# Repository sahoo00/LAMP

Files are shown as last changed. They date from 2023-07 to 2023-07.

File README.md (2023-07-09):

# LAMP
A RT-LAMP device for quantitative mRNA measurement at home

## General Info
This folder has EAGLE files for a hardware device that can measure mRNA
at home. There are two modules: Camera and LAMP. Arduino codes, 
Board and Schematic files
for both these modules are provided. CAM processor outputs of all the files
are provided in CAMOutputs.

## Software requirements
Project is created with
* EAGLE
* Adobe Illustrator
* Fusion 360
* Arduino IDE

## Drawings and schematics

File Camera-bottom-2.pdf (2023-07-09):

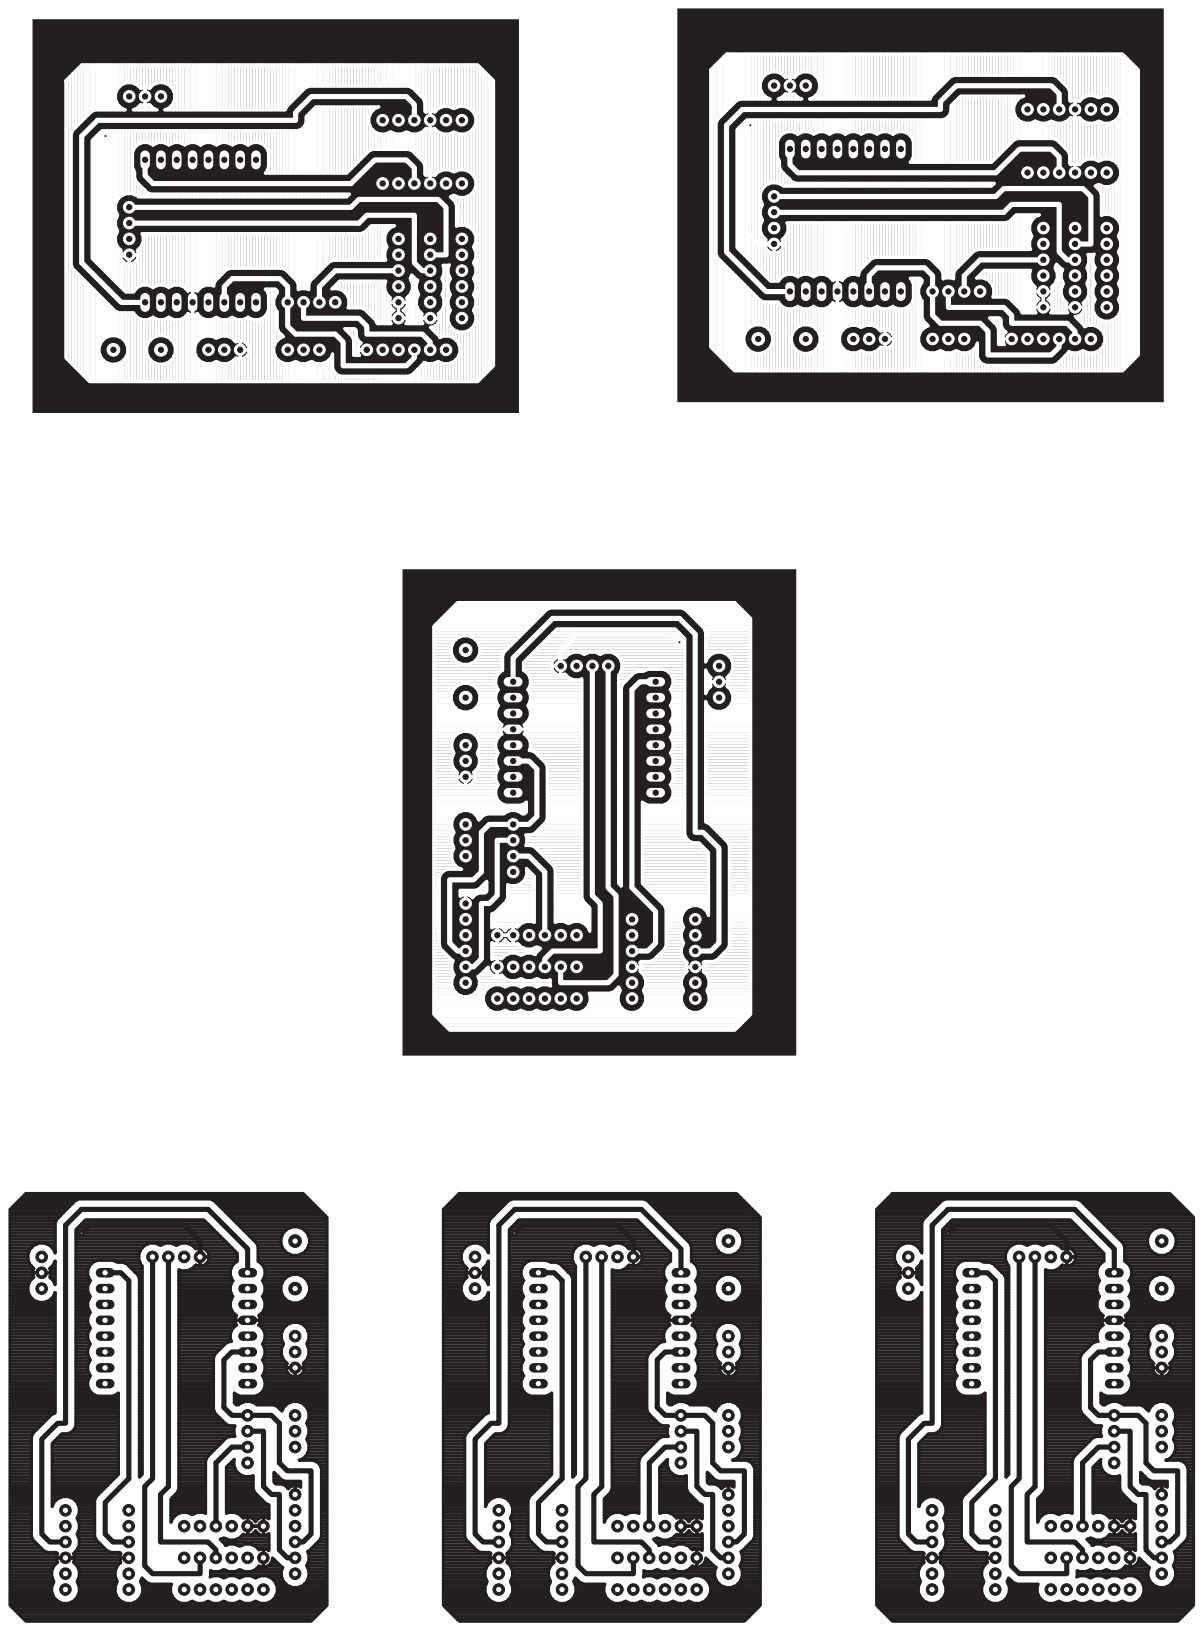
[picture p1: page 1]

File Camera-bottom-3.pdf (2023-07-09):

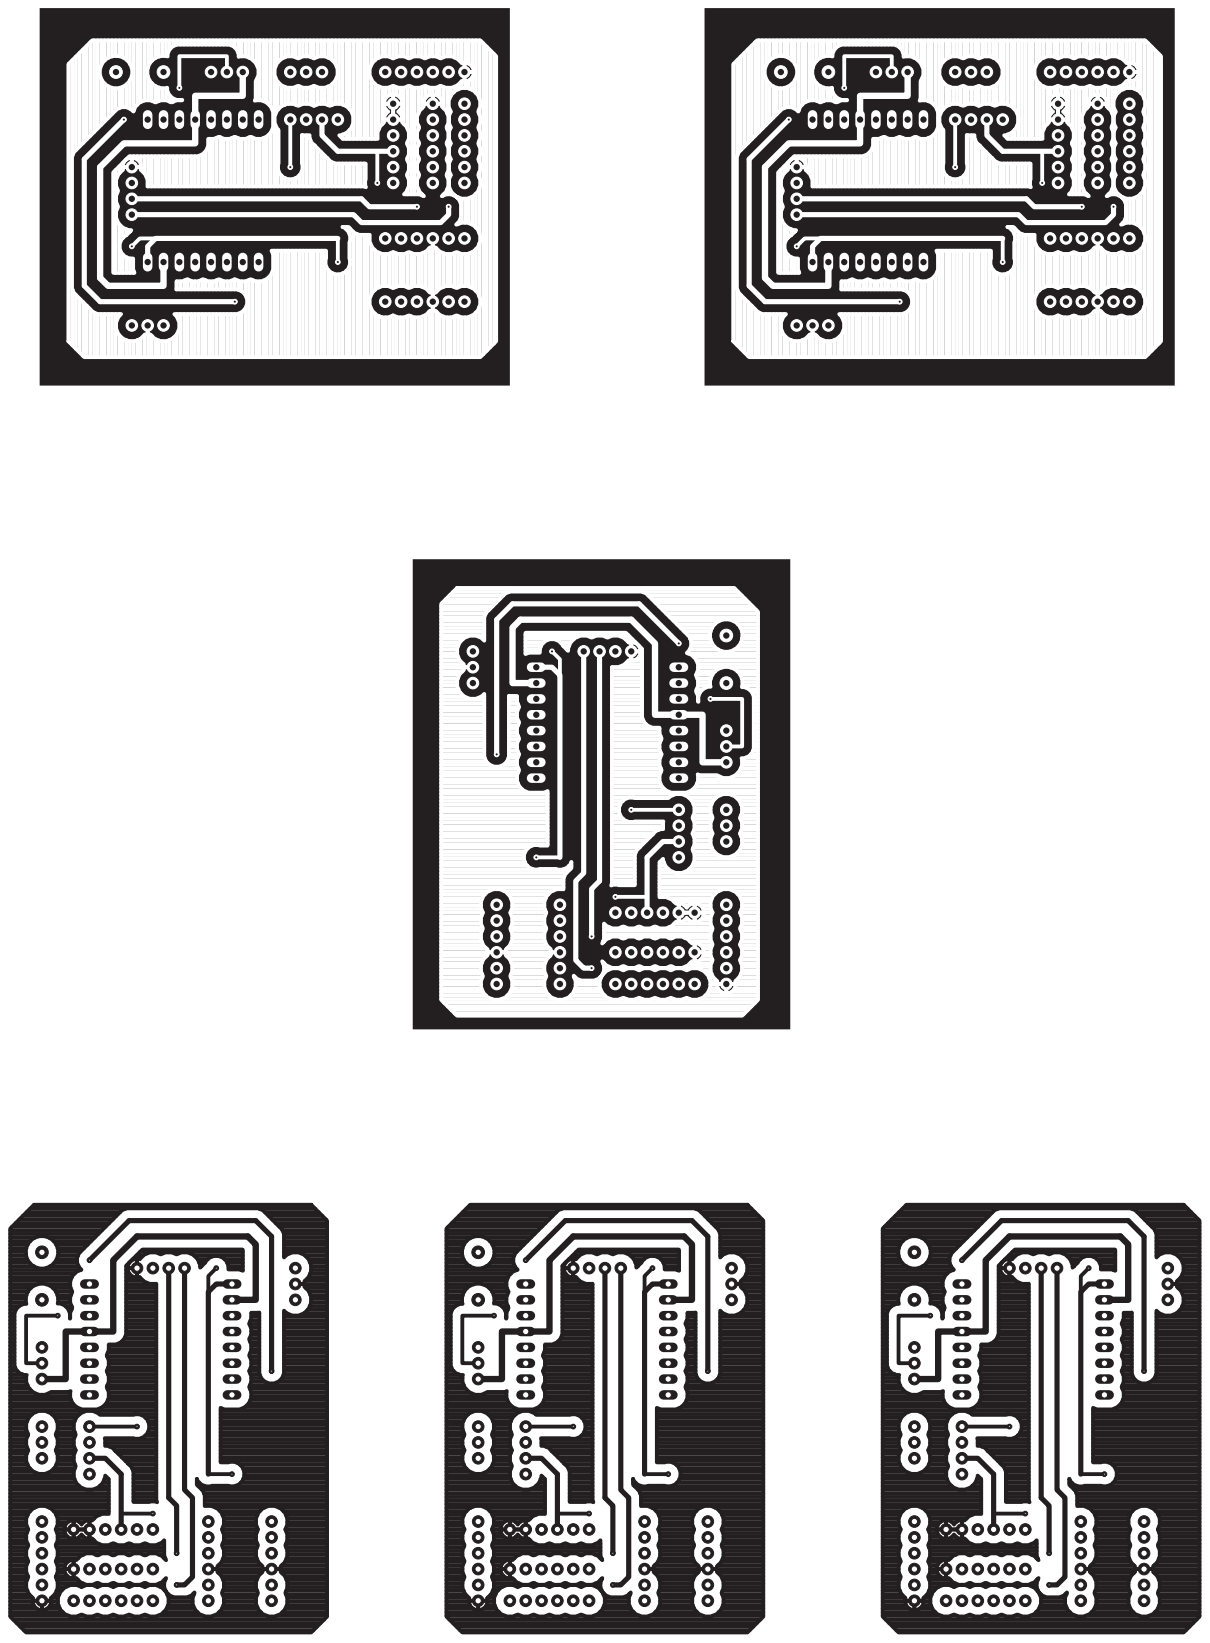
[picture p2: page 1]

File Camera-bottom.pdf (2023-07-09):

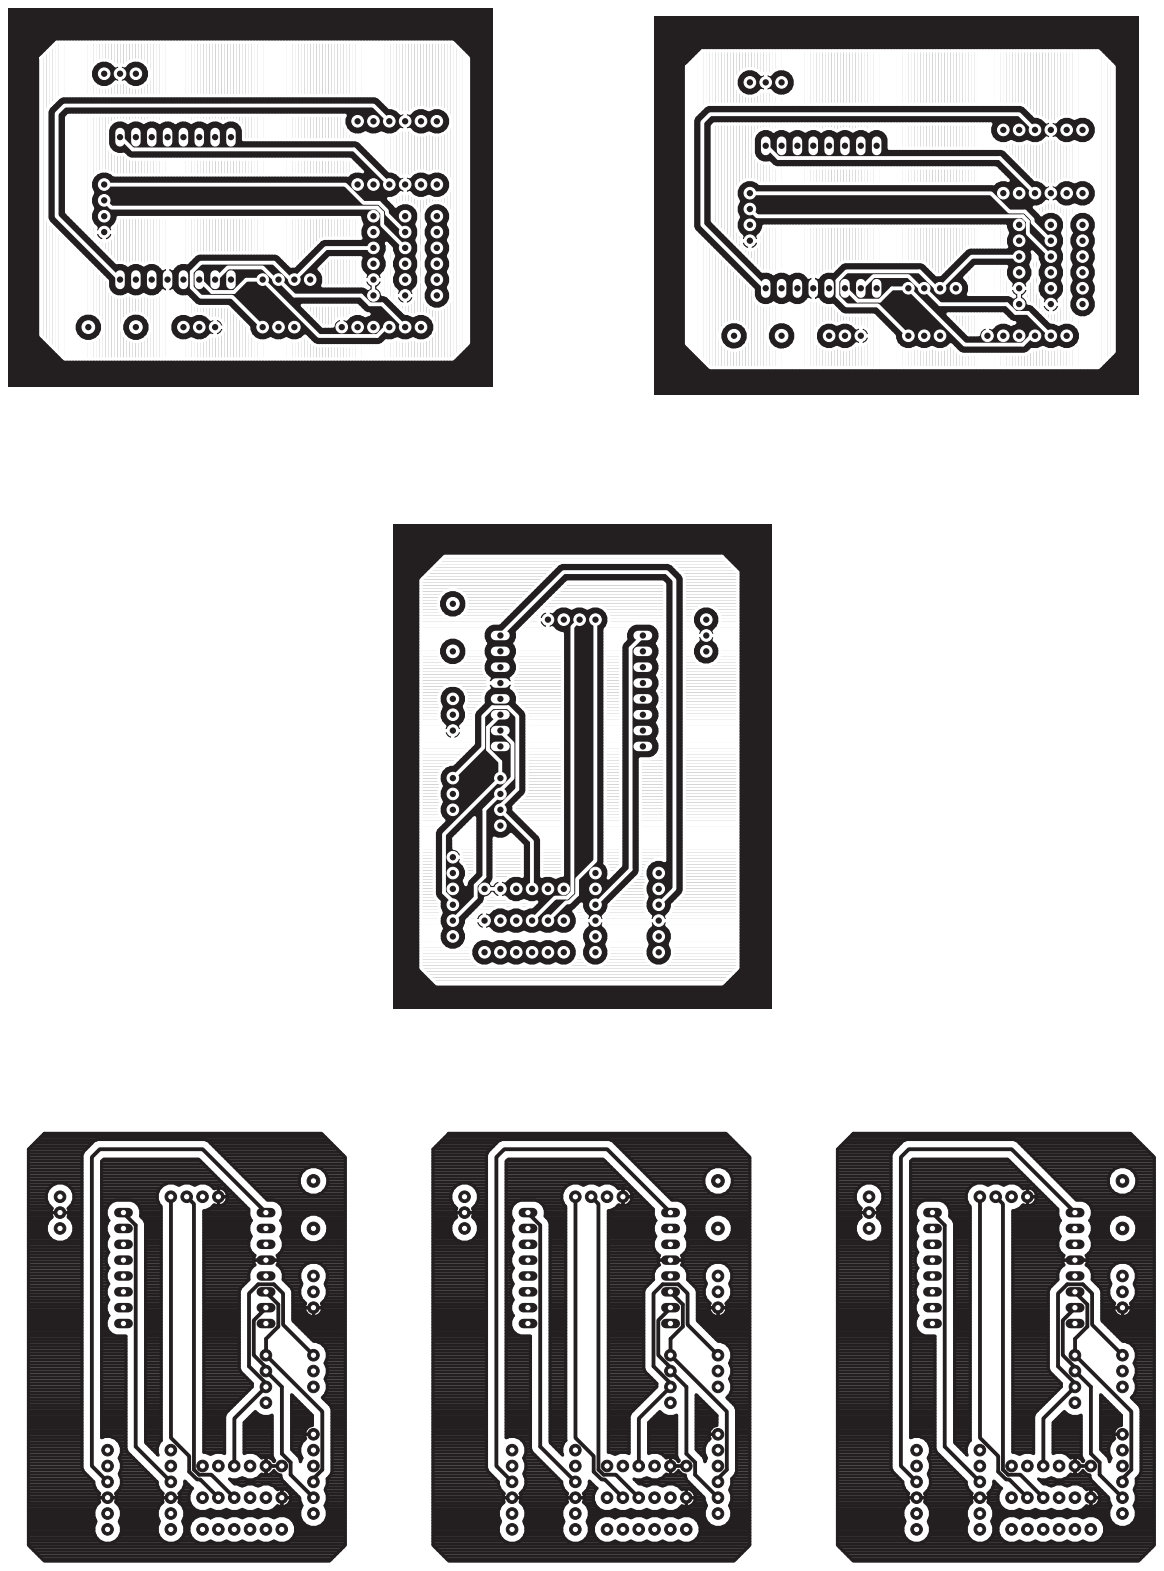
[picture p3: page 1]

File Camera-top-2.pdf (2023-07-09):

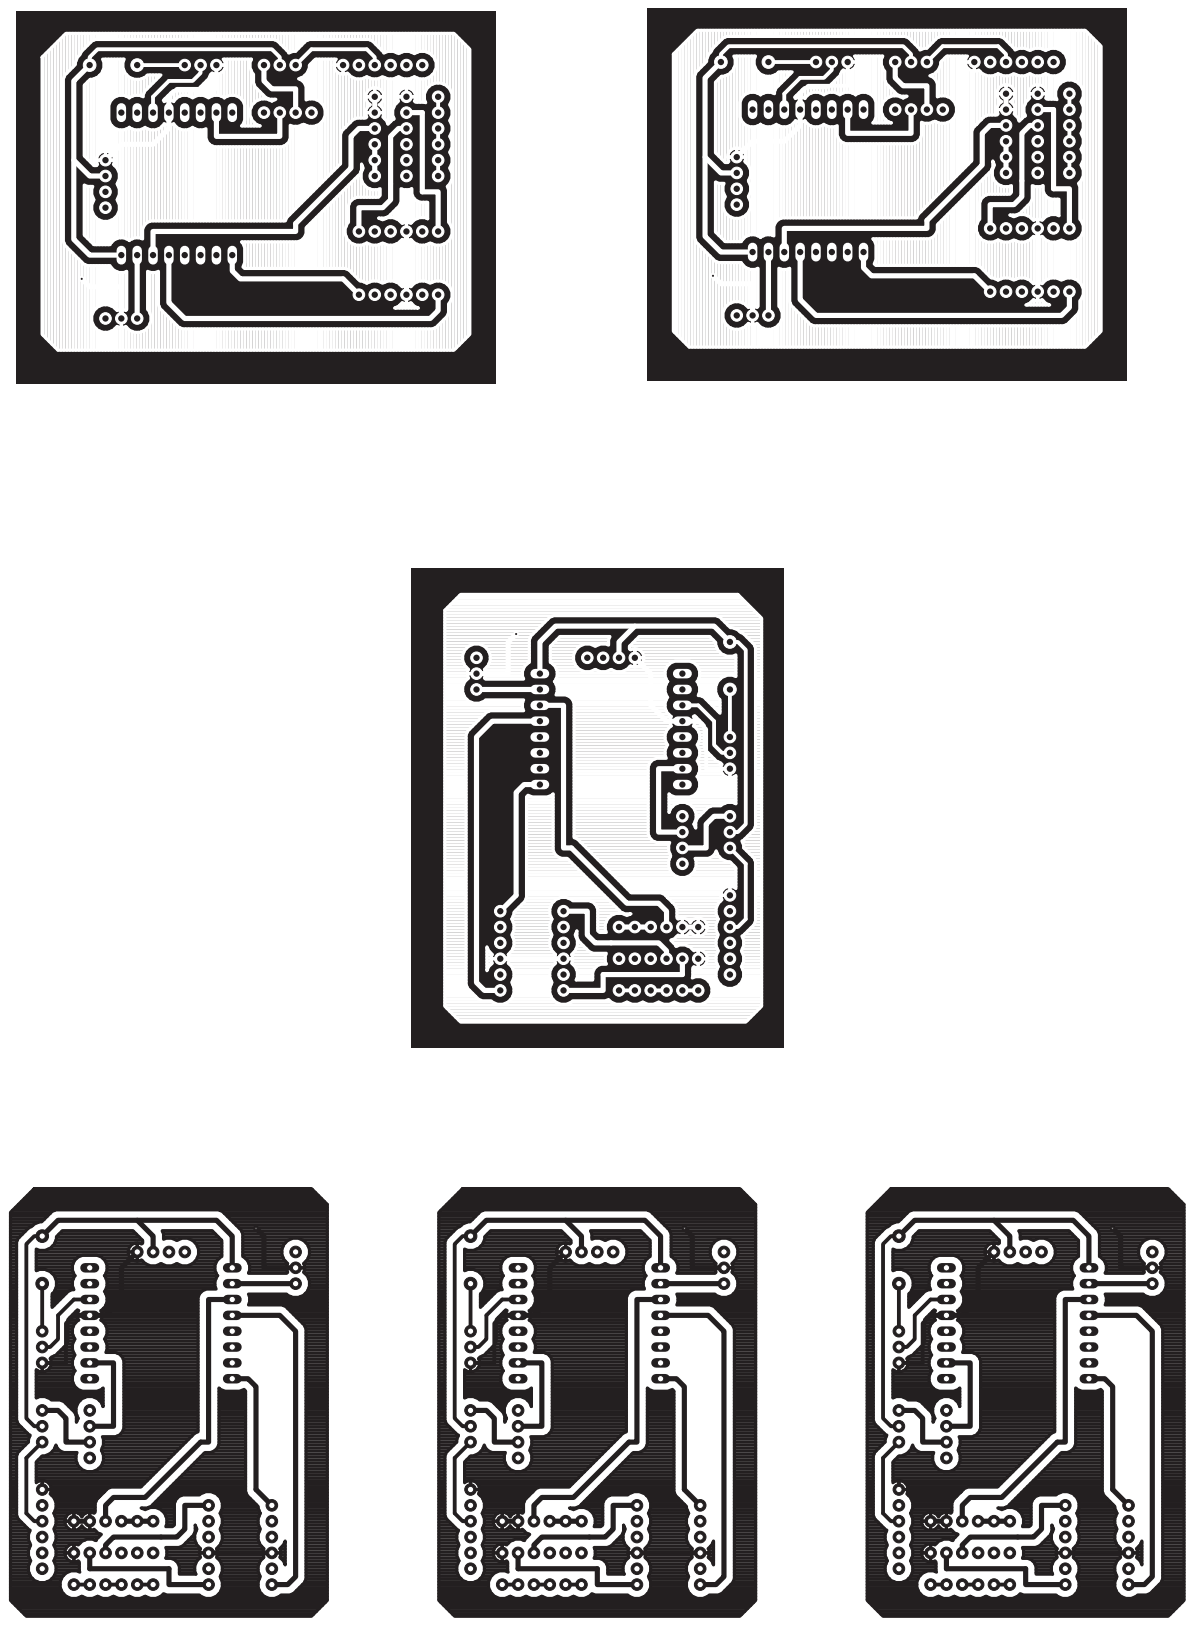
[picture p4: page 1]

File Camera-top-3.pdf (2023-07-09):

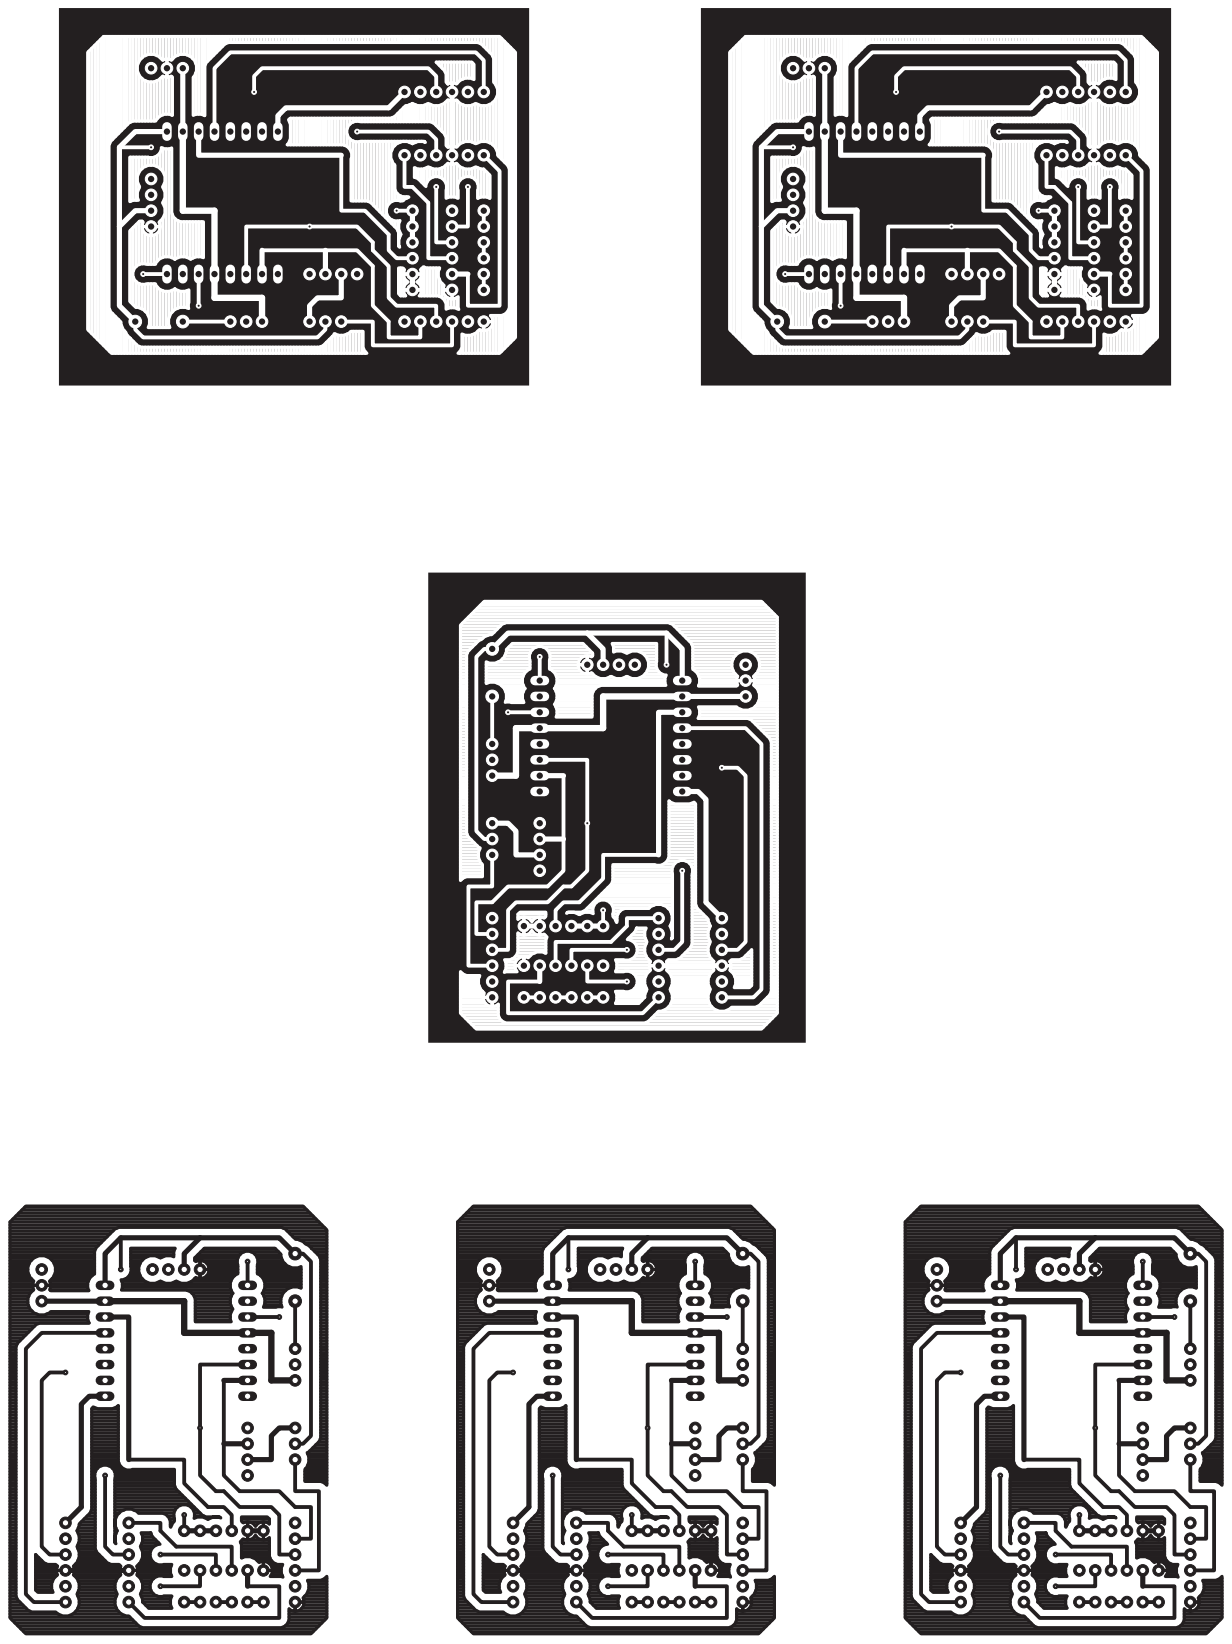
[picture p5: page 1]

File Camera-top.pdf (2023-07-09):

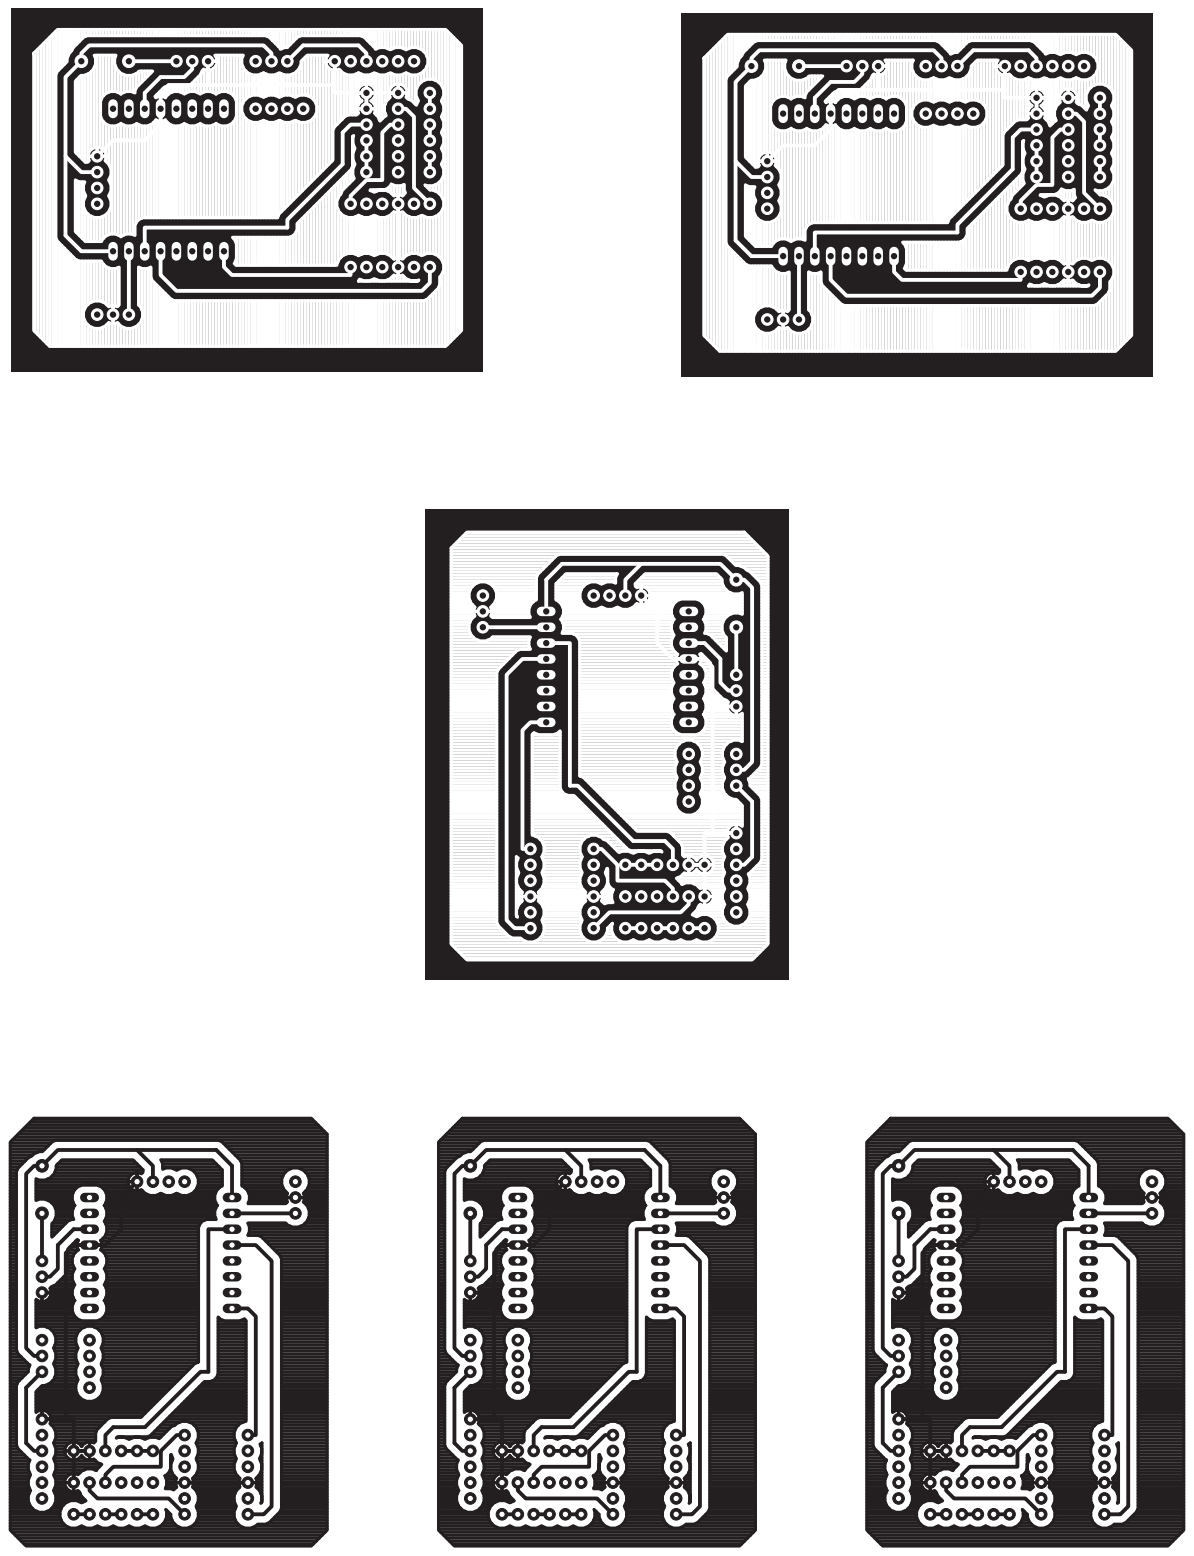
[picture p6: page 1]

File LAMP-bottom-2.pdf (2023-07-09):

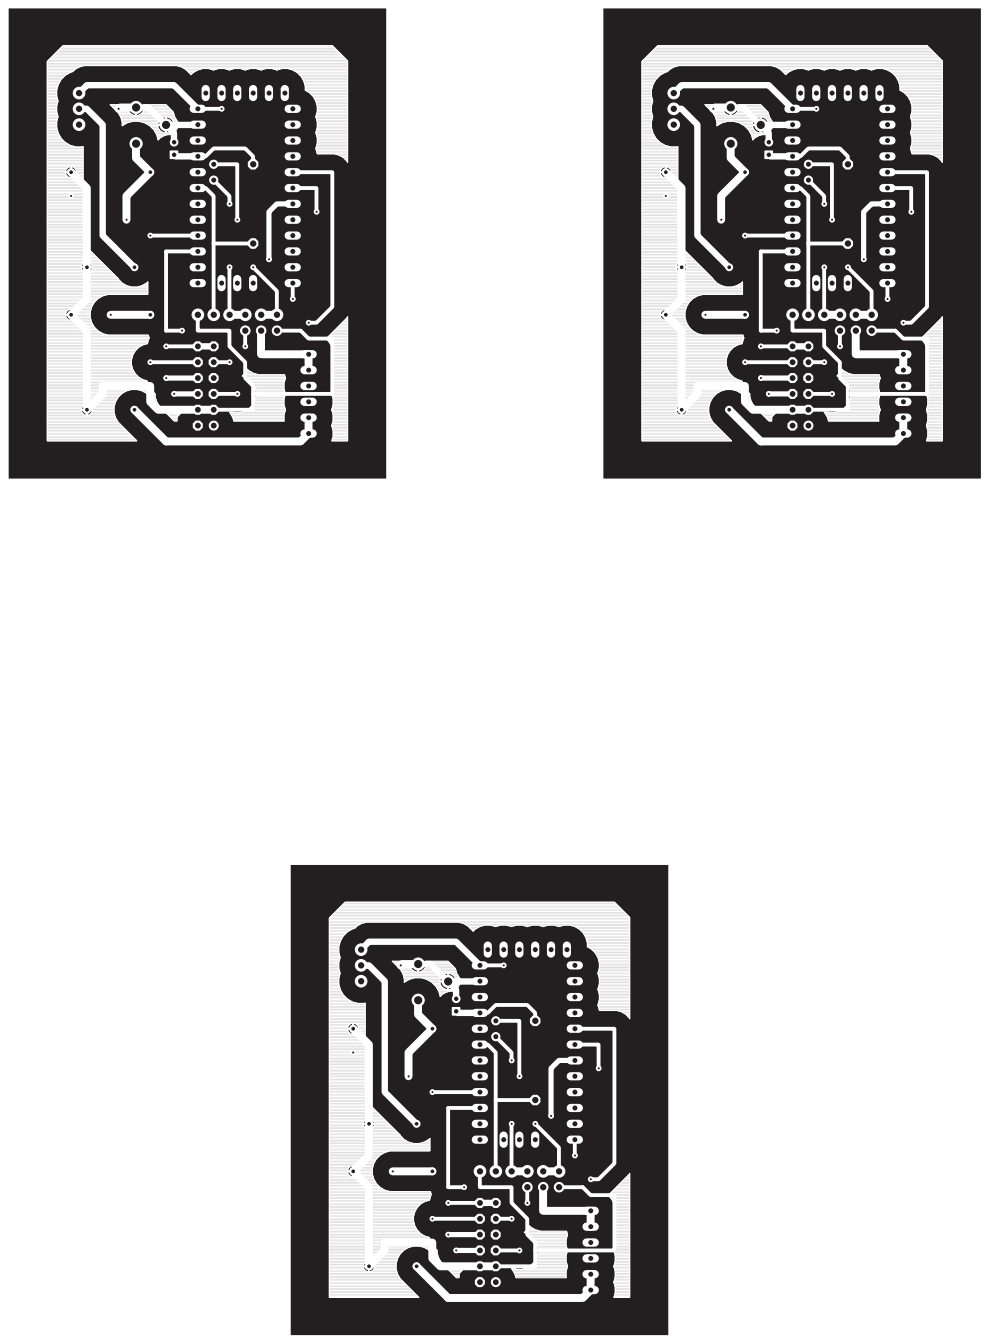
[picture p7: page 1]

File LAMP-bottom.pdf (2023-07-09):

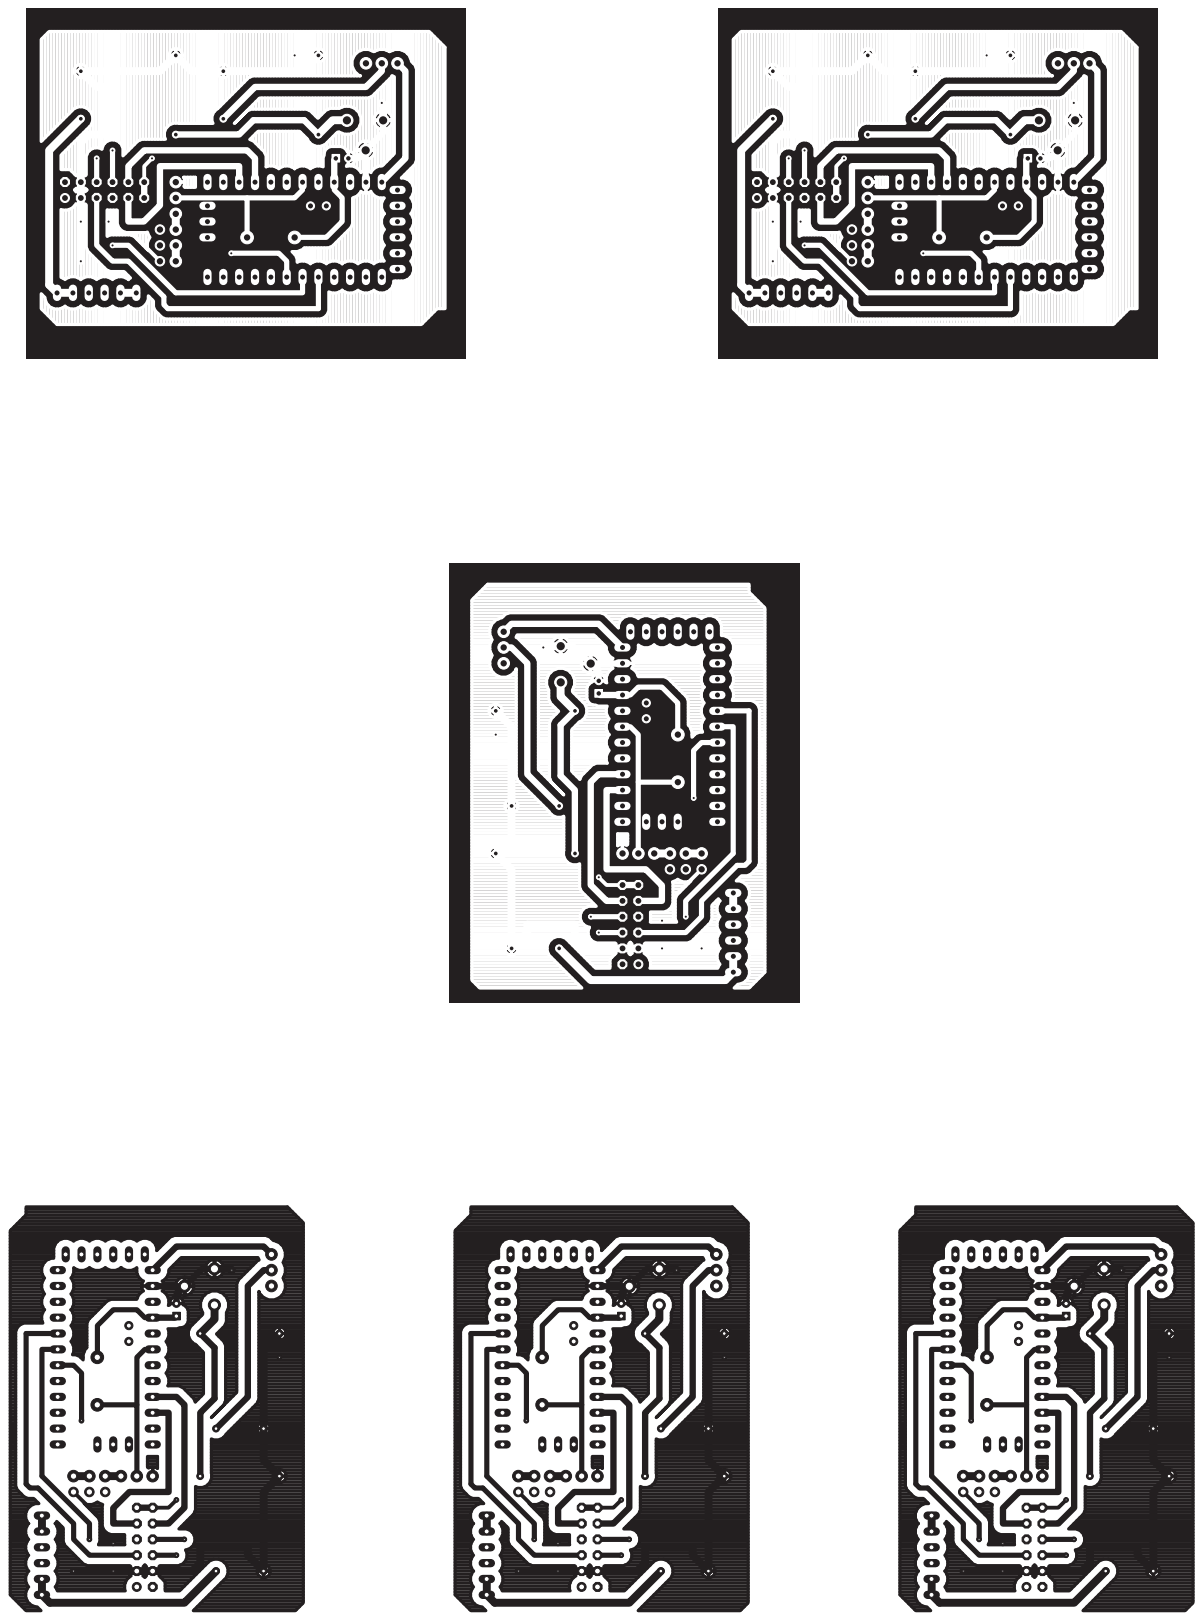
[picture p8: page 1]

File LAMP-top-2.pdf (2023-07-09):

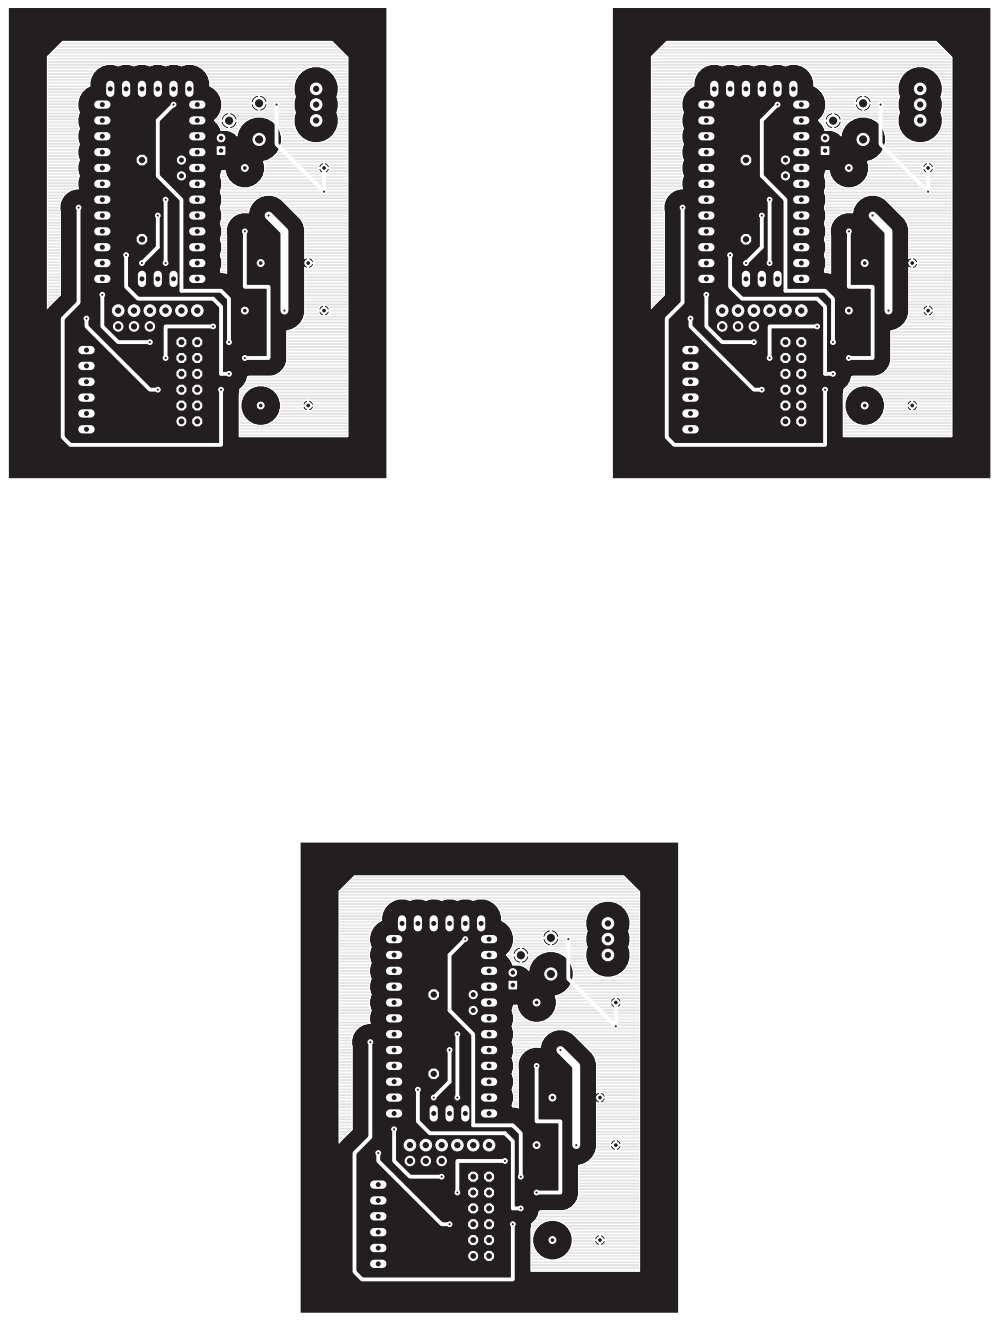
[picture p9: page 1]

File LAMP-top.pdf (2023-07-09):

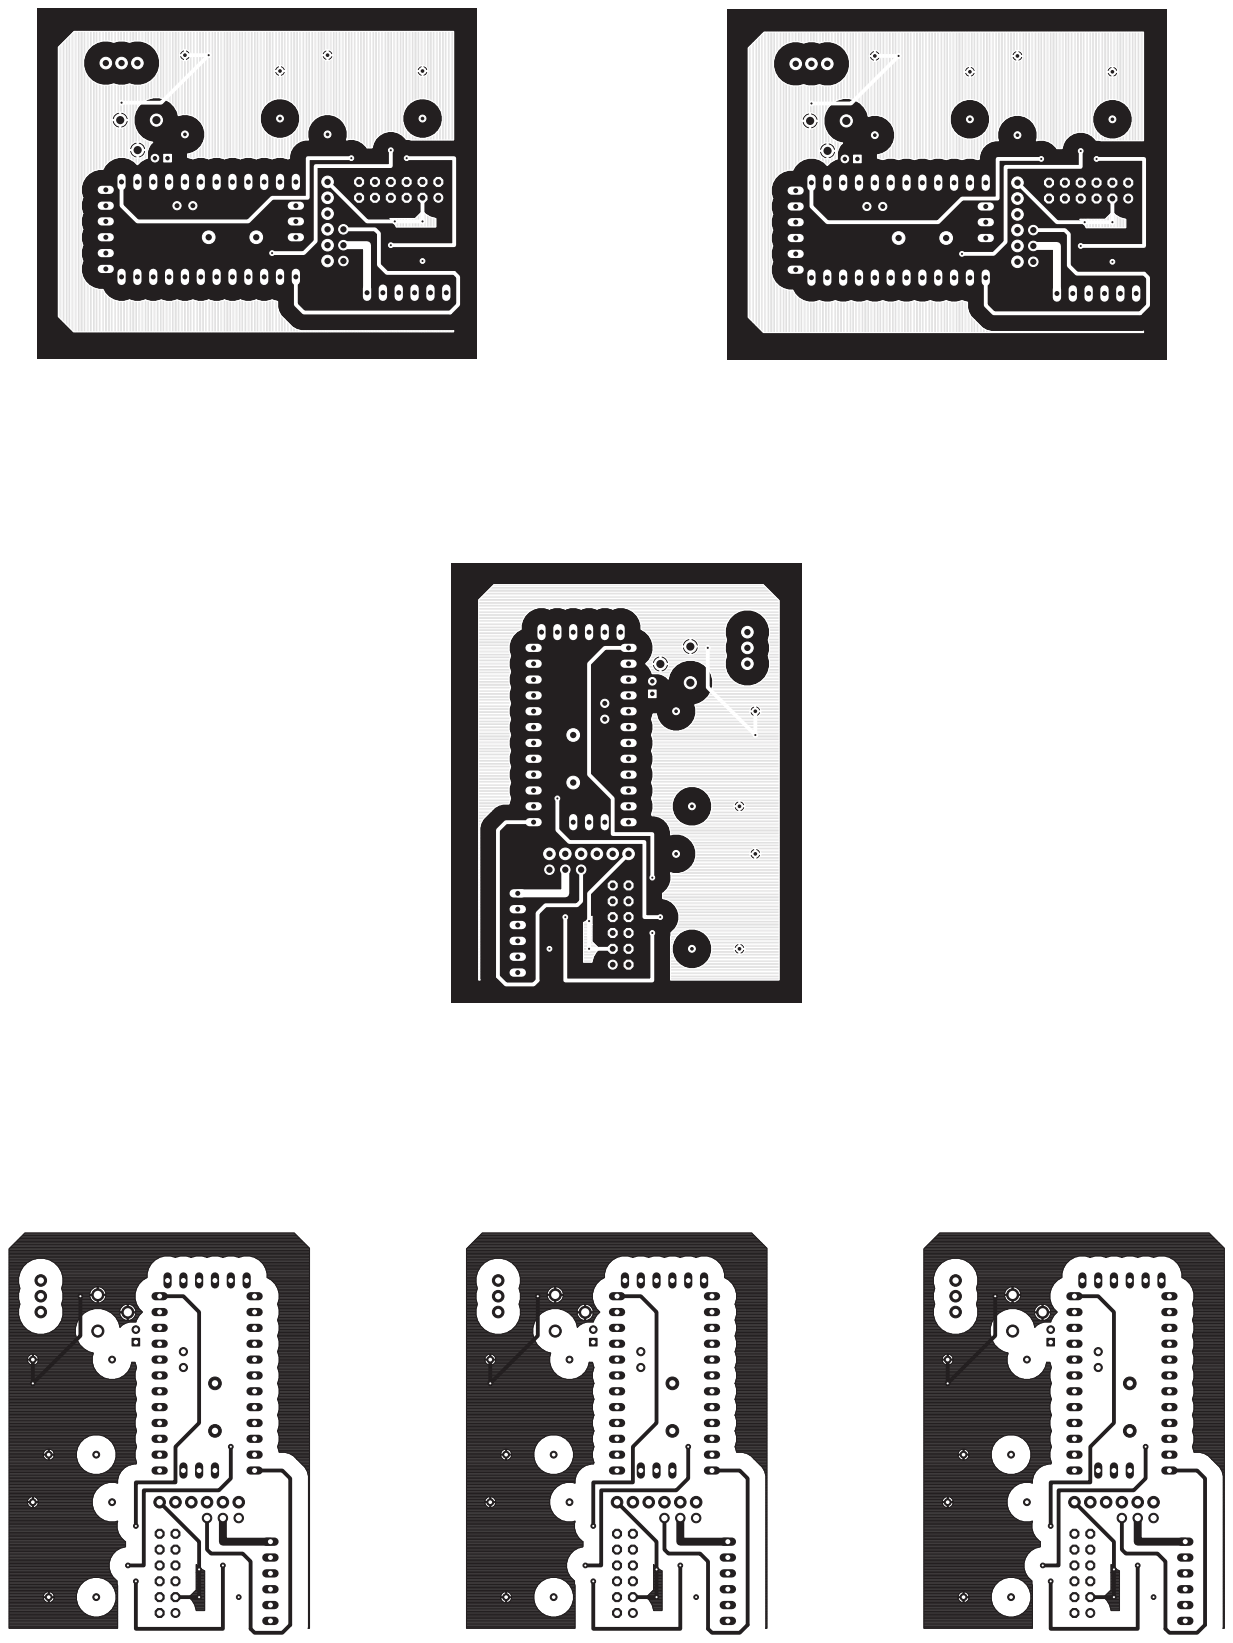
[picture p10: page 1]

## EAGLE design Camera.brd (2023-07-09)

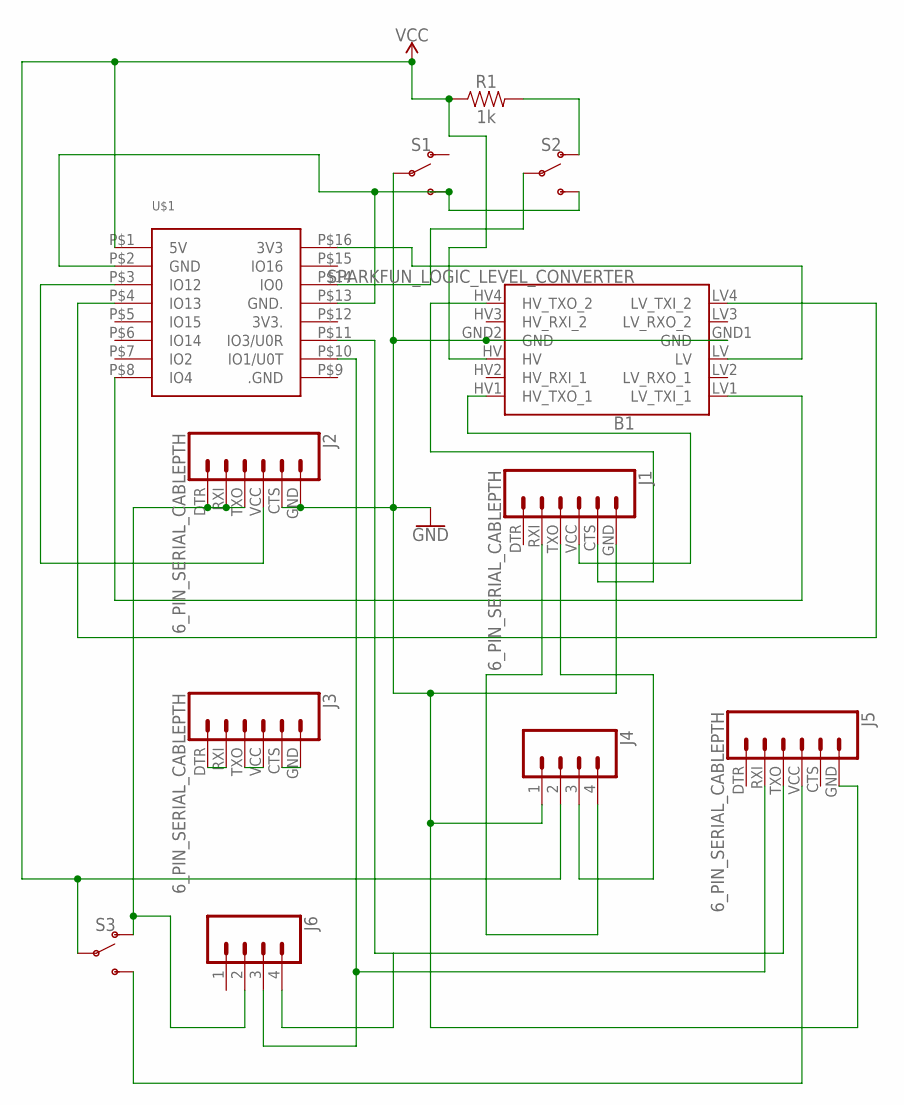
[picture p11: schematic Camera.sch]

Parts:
B1: SPARKFUN_LOGIC_LEVEL_CONVERTER
J1, J2, J3, J5: 6_PIN_SERIAL_CABLEPTH; FTDI_BASIC
J4, J6: CONN_04PTH; 1X04
R1: 1k; AXIAL-0.3-KIT
S1, S2, S3: SWITCH-SPDT-PTH-11.6X4.0MM; SWITCH_SPDT_PTH_11.6X4.0MM
U$1: ESP32-CAM

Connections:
GND: B1.GND1 (GND), B1.GND2 (GND), J1.GND (6), J2.CTS (5), J2.GND (6), J4.1, J5.GND (6), S1.2
unnamed: R1.P$2 (2), S2.1 (O)
unnamed: S1.3 (S), S2.3 (S), U$1.P$2 (GND), U$1.P$13 (GND.)
unnamed: J3.DTR (1), J3.RXI (2)
unnamed: S2.2, U$1.P$14 (IO0)
unnamed: J3.TXO (3), J3.VCC (4)
unnamed: B1.LV1 (LV_TXI_1), U$1.P$8 (IO4)
unnamed: B1.LV4 (LV_TXI_2), U$1.P$4 (IO13)
unnamed: J3.CTS (5), J3.GND (6)
unnamed: J2.VCC (4), U$1.P$3 (IO12)
unnamed: B1.HV1 (HV_TXO_1), J1.VCC (4)
unnamed: B1.HV4 (HV_TXO_2), J1.CTS (5)
unnamed: J1.RXI (2), J4.4
unnamed: J1.TXO (3), J4.3
unnamed: B1.LV, U$1.P$16 (3V3)
unnamed: J5.TXO (3), J6.4, U$1.P$11 (IO3/U0R)
unnamed: J5.RXI (2), J6.3, U$1.P$10 (IO1/U0T)
unnamed: J2.DTR (1), J2.RXI (2), J2.TXO (3), J6.2, S3.1 (O)
unnamed: J5.VCC (4), S3.3 (S)
VCC: B1.HV, J4.2, R1.P$1 (1), S3.2, U$1.P$1 (5V)

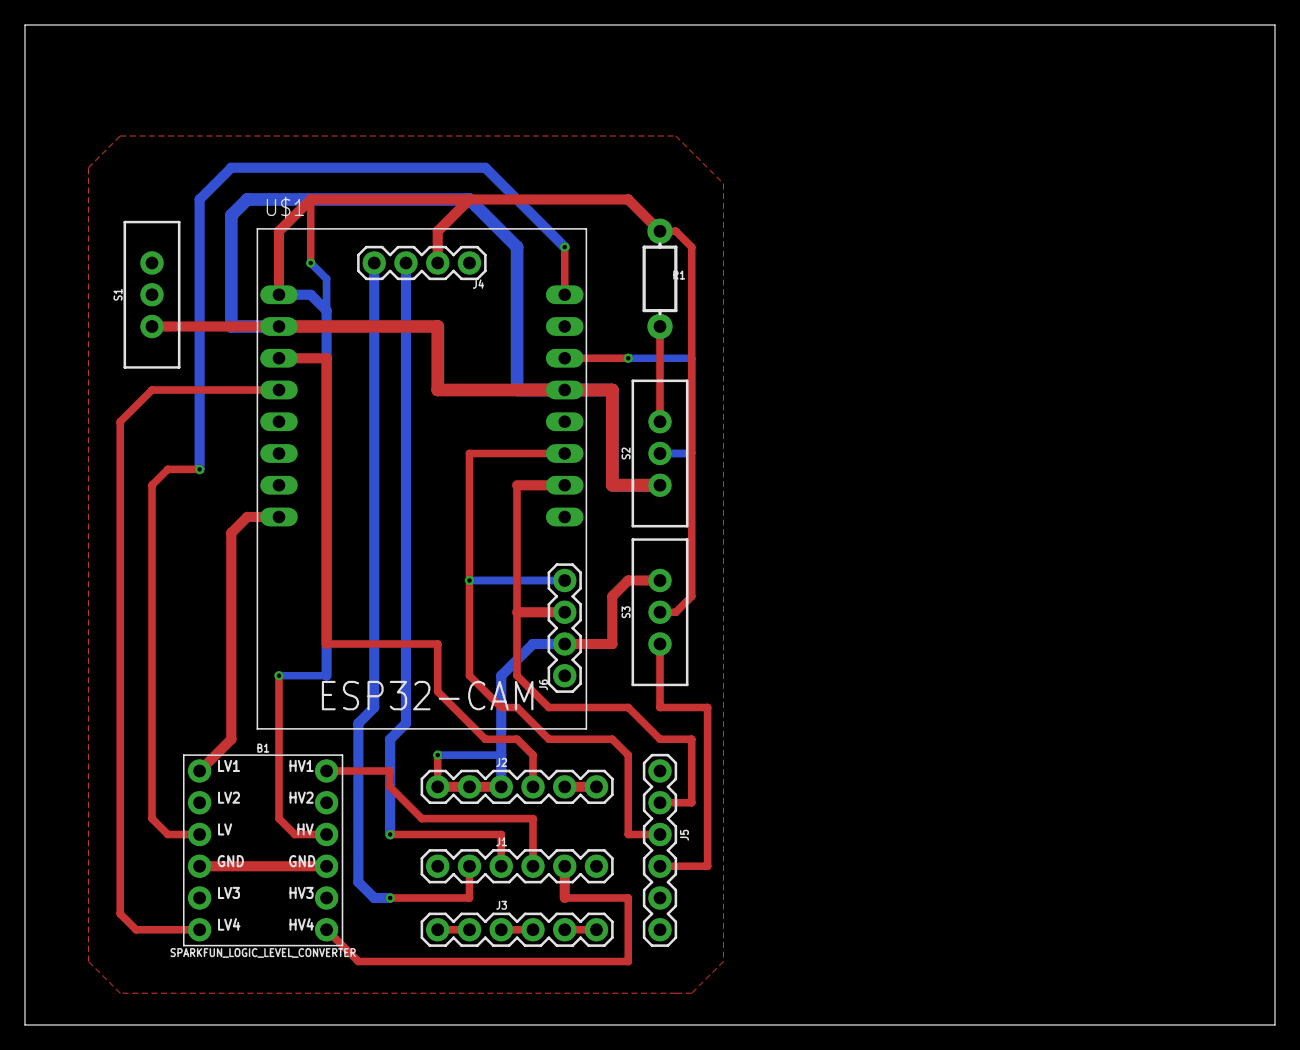
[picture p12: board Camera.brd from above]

Board: 2 copper layers, 100.0 x 80.0 mm, 12 parts (0 on the bottom side), 20 nets.

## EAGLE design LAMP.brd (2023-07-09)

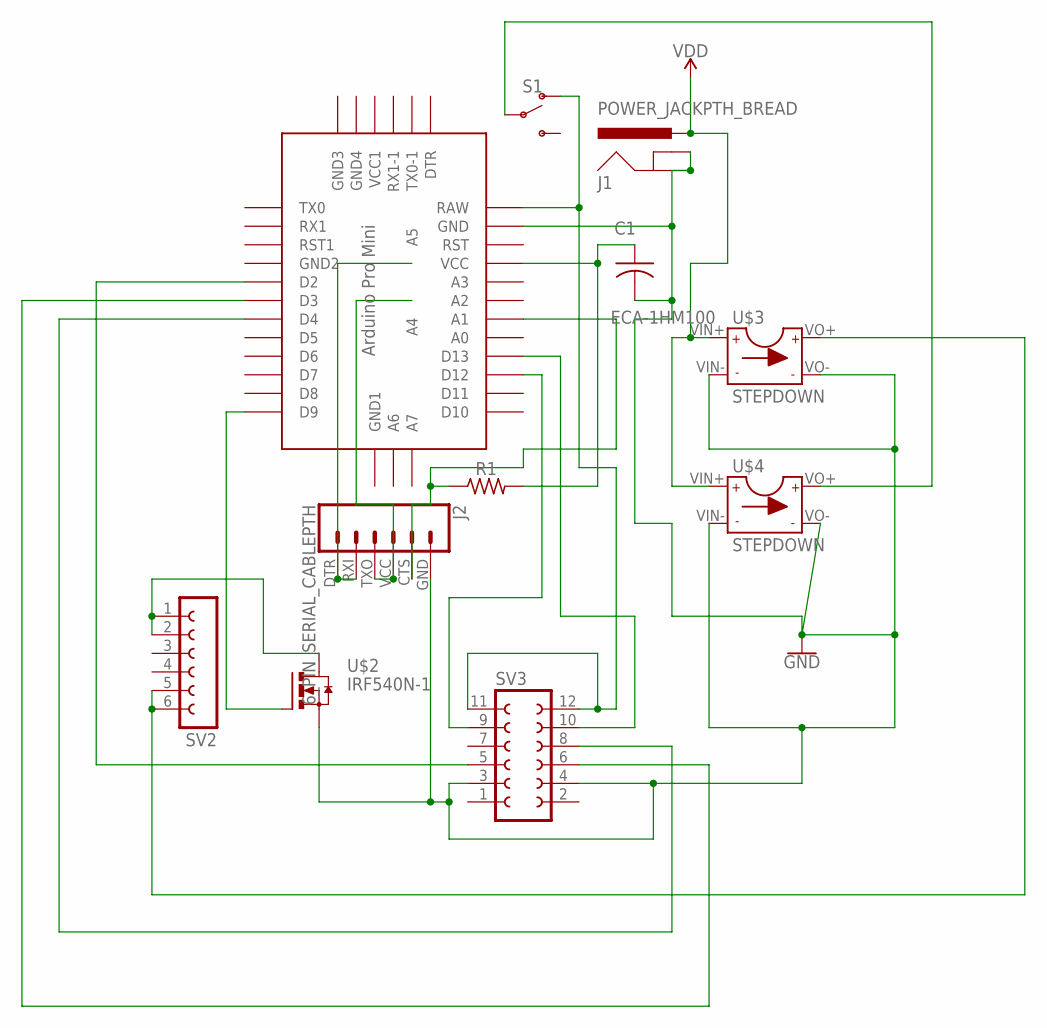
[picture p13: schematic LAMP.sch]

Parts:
C1: ECA-1HM100; CAP_RADIAL_2MM
J1: POWER_JACKPTH_BREAD; POWER_JACK_PTH_BREAD
J2: 6_PIN_SERIAL_CABLEPTH; FTDI_BASIC
R1: 1k; V234/12
S1: SWITCH-SPDT-PTH-11.6X4.0MM; SWITCH_SPDT_PTH_11.6X4.0MM
SV2: FE06-1; FE06
SV3: FE06-2
U$1: ABK-PRO-MINI-2
U$2: IRF540N-1; 1X03
U$3, U$4: STEPDOWN; STEPDOWN-1

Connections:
GND: C1.2, J1.GND, J1.GNDBREAK, J2.GND (6), SV3.3, SV3.4, U$1.GND, U$2.3 (S), U$3.VIN-, U$3.VO-, U$4.VIN-, U$4.VO-
unnamed: S1.2, U$4.VO+
unnamed: S1.1 (O), SV3.11, SV3.12, U$1.RAW
unnamed: SV2.1, SV2.2, U$2.2 (D)
unnamed: J2.DTR (1), J2.RXI (2), U$1.A5
unnamed: U$1.D9, U$2.1 (G)
unnamed: SV3.9, U$1.D12
unnamed: SV2.5, SV2.6, U$3.VO+
unnamed: SV3.10, U$1.D13
unnamed: J2.CTS (5), R1.1, U$1.A1
unnamed: C1.1, R1.2, U$1.VCC
unnamed: SV3.5, U$1.D2
unnamed: SV3.6, U$1.D3
unnamed: SV3.8, U$1.D4
unnamed: J2.TXO (3), J2.VCC (4), U$1.A4
VDD: J1.PWR, U$3.VIN+, U$4.VIN+

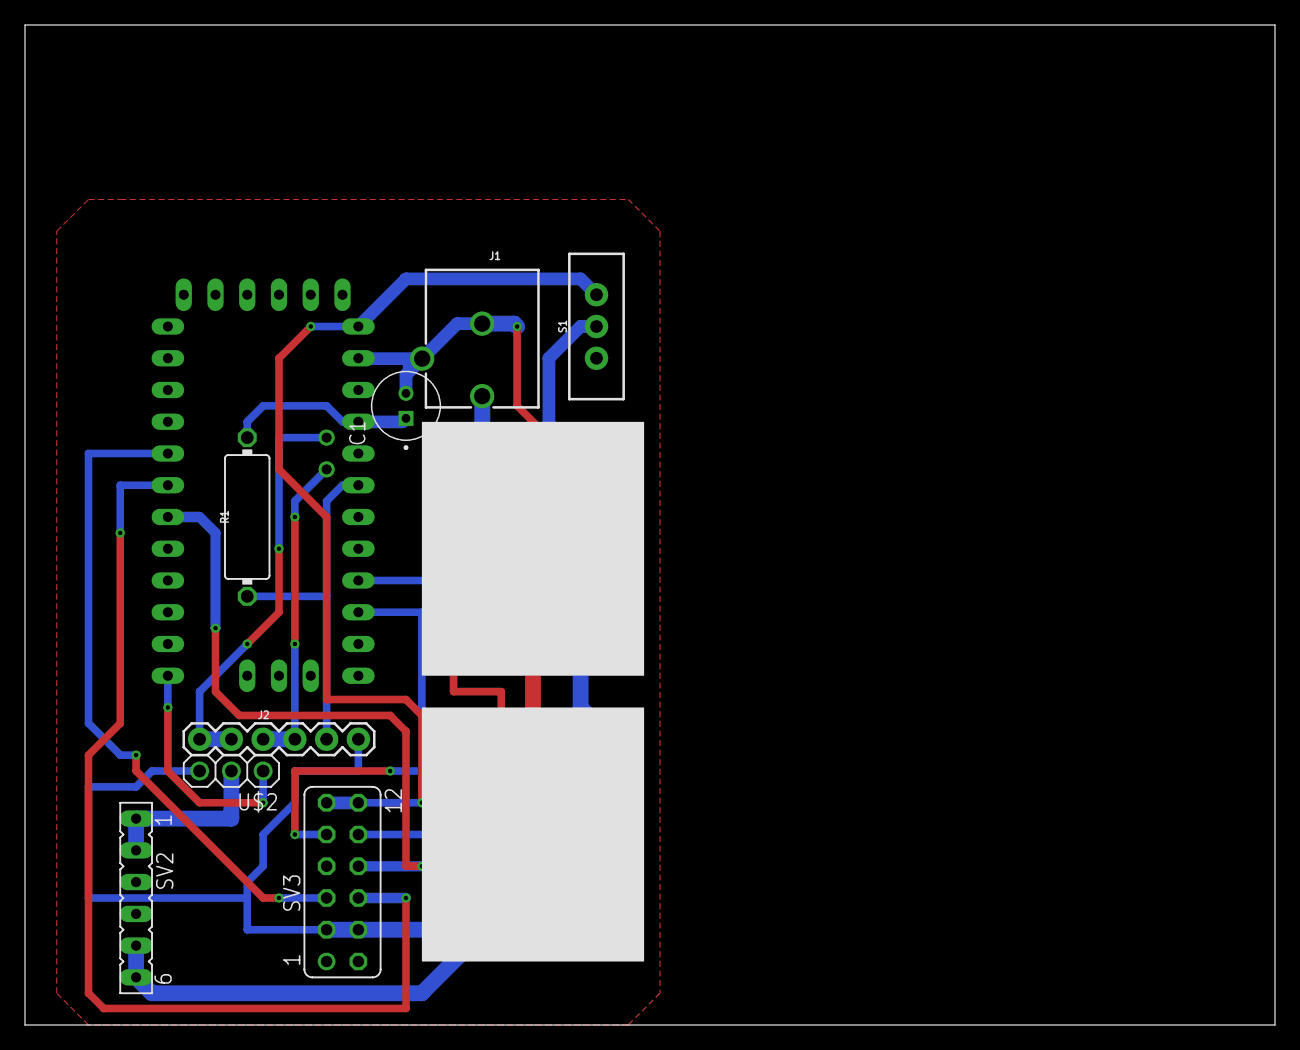
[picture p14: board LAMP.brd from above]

Board: 2 copper layers, 100.0 x 80.0 mm, 11 parts (0 on the bottom side), 16 nets.

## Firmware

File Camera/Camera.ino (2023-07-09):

/*********
  Rui Santos
  Complete project details at https://RandomNerdTutorials.com/esp32-cam-take-photo-display-web-server/
  
  IMPORTANT!!! 
   - Select Board "AI Thinker ESP32-CAM"
   - GPIO 0 must be connected to GND to upload a sketch
   - After connecting GPIO 0 to GND, press the ESP32-CAM on-board RESET button to put your board in flashing mode
  
  The above copyright notice and this permission notice shall be included in all
  copies or substantial portions of the Software.
*********/

#include "WiFi.h"
#include "esp_camera.h"
#include "esp_timer.h"
#include "img_converters.h"
#include "Arduino.h"
#include "FS.h"                // SD Card ESP32
#include "SD_MMC.h"            // SD Card ESP32
#include "soc/soc.h"           // Disable brownour problems
#include "soc/rtc_cntl_reg.h"  // Disable brownour problems
#include "driver/rtc_io.h"
#include <WebServer.h>
#include <Ticker.h>
#include <Adafruit_GFX.h>
#include <Adafruit_SSD1306.h>
#include <CommandHandler.h>

// define the number of bytes you want to access
#define EEPROM_SIZE 1

#define DEBUG
#include "DebugMacros.h"

#include <Wire.h>

// Replace with your network credentials
//const char* ssid = "DSSP-Home";
//const char* password = "260604072013";
const char* ssid = "Pixel_8154";
const char* password = "Shanvi123!";

const char* apssid = "ActiveGene";
const char* appassword = "BooleanLab";

const char* jquery = "/jquery-3.1.0.min.js";

class SWebServer: public WebServer {
  protected:
  void _addMHeader(String &header, String hdr) {
    header = header.substring(0, header.length()-3) + hdr + "\r\n";
  }
  void _addMHeader(String &header, String t, String val) {
    _addMHeader(header, t + ": " + val + "\r\n");
  }
  
  public:
  SWebServer(int port): WebServer(port) {}
  void send(int code, const char* content_type, const String& content) {
    WebServer::send(code, content_type, content);
  }
  
  void send(int code, char* content_type, String hdr, const char * buf, size_t len) {
    String header;
    _prepareHeader(header, code, content_type, len);
    //header = header.substring(0, header.length()-3) + hdr + "\r\n";
    _addMHeader(header, hdr);
    _currentClient.write(header.c_str(), header.length());
    if(len > 0) {
      const char * footer = "\r\n";
      if(_chunked) {
        char * chunkSize = (char *)malloc(11);
        if(chunkSize){
          sprintf(chunkSize, "%x%s", len, footer);
          _currentClient.write(chunkSize, strlen(chunkSize));
          free(chunkSize);
        }
      }
      _currentClient.write(buf, len);
      if(_chunked){
        _currentClient.write(footer, 2);
      }
    }
  }

  void send(FS &fs, const String& path, char * contentType, bool download) {
    int code = 200;  
    File file = fs.open(path, "r");
    int len = file.size();
    
    String header;
    _prepareHeader(header, code, contentType, len);

    int filenameStart = path.lastIndexOf('/') + 1;
    char buf[26+path.length()-filenameStart];
    char* filename = (char*)path.c_str() + filenameStart;
    if(download) {
      // set filename and force download
      snprintf(buf, sizeof (buf), "attachment; filename=\"%s\"", filename);
    } else {
      // set filename and force rendering
      snprintf(buf, sizeof (buf), "inline; filename=\"%s\"", filename);
    }
    _addMHeader(header, "Content-Disposition", String(buf));
    _currentClient.write(header.c_str(), header.length());
  
    if(len > 0) {
      _currentClient.write(file);
    }
  }
};

// Create WebServer object on port 80
SWebServer server(80);
File root;
bool opened = false;

int pictureNumber = 0;
int recordPictures = 0;
int sdcard_present = 1;
Ticker scheduler;
#define LED_PIN 12
#define RXD2 13
#define TXD2 4
CommandHandler<4, 20, 0> SerialCommandHandler(Serial2, '!', '\n');
IPAddress _s_ip;                    // the IP address of your shield

// OV2640 camera module pins (CAMERA_MODEL_AI_THINKER)
#define PWDN_GPIO_NUM     32
#define RESET_GPIO_NUM    -1
#define XCLK_GPIO_NUM      0
#define SIOD_GPIO_NUM     26
#define SIOC_GPIO_NUM     27
#define Y9_GPIO_NUM       35
#define Y8_GPIO_NUM       34
#define Y7_GPIO_NUM       39
#define Y6_GPIO_NUM       36
#define Y5_GPIO_NUM       21
#define Y4_GPIO_NUM       19
#define Y3_GPIO_NUM       18
#define Y2_GPIO_NUM        5
#define VSYNC_GPIO_NUM    25
#define HREF_GPIO_NUM     23
#define PCLK_GPIO_NUM     22

const char index_html[] PROGMEM = R"rawliteral(
<!DOCTYPE HTML><html>
<head>
  <meta name="viewport" content="width=device-width, initial-scale=1">
  <style>
    body { text-align:center; }
    .vert { margin-bottom: 10%; }
    .hori{ margin-bottom: 0%; }
  </style>
  <script src="https://code.jquery.com/jquery-3.1.0.min.js" type="text/javascript"></script>
  <script src="jquery" type="text/javascript"></script>
  <script type="text/javascript">
  function sendLED() {
    var url = "led?num=" + $("#photoNum").val();
    $("#results").load(url);
    return false;
  }
  function updateImage() {
    var url = "capture-photo";
    $("#photo").attr("src", url + `?v=${new Date().getTime()}`);
    return false;
  }
  function sendSave() {
    var url = "save-photo?num=" + $("#photoNum").val();
    $("#results").load(url);
    return false;
  }
  function sendRecord() {
    var url = "record-start";
    $("#results").load(url);
    return false;
  }
  function sendStop() {
    var url = "record-stop";
    $("#results").load(url);
    return false;
  }
  function sendReset() {
    var url = "reset?num=" + $("#photoNum").val();
    $("#results").load(url);
    return false;
  }
  function getInfo() {
    var url = "get-info?num=" + $("#photoNum").val();
    $("#results").load(url);
    return false;
  }
  function getPhoto() {
    var url = "get-photo?num=" + $("#photoNum").val();
    $("#photo").removeAttr("src").attr("src", url);
    return false;
  }
  </script>
</head>
<body>
  <div id="container">
    <h2>ESP32-CAM Photo Capture</h2>
    <p>
      <button onclick="sendLED();">LED</button>
      <button onclick="updateImage();">Capture</button>
      <button onclick="sendSave();">Save</button>
      <button onclick="sendRecord();">Record</button>
      <button onclick="sendStop();">Stop</button>
      <button onclick="sendReset();">Reset</button>
      <button onclick="getInfo();">GetInfo</button>
      <button onclick="getPhoto();">Get</button>
      Num:<input type="text" size="4" id="photoNum" name="num" value="0"/>
    </p>
  </div>
  <div id="results"></div>
  <div><img src="capture-photo" id="photo" width="70%"></div>
  <br/>
<form method='POST' action='#' enctype='multipart/form-data' id='upload_form'>
<input type='file' name='update'>
<input type='submit' value='Upload'>
</form>
<div id='prg'>progress: 0%</div>
<script>
$('form').submit(function(e){
    e.preventDefault();
    var form = $('#upload_form')[0];
    var data = new FormData(form);
    $.ajax({
          url: '/update',
          type: 'POST',
          data: data,
          contentType: false,
          processData:false,
          xhr: function() {
              var xhr = new window.XMLHttpRequest();
              xhr.upload.addEventListener('progress', function(evt) {
                  if (evt.lengthComputable) {
                      var per = evt.loaded / evt.total;
                      $('#prg').html('progress: ' + Math.round(per*100) + '%');
                  }
             }, false);
             return xhr;
          },
          success:function(d, s) {
              console.log('success!')
          },
          error: function (a, b, c) {
          }
    });
});
</script>
</body>
</html>)rawliteral";

void savePicture(int num) {
  camera_fb_t * fb = NULL;

  if (sdcard_present == 0) {
    return;
  }
  
  // Take Picture with Camera
  fb = esp_camera_fb_get();  
  if(!fb) {
    DPRINTLN("Camera capture failed");
    return;
  }

  // Path where new picture will be saved in SD Card
  String path = "/picture-" + String(num) +".jpg";

  fs::FS &fs = SD_MMC;
#ifdef DEBUG
  Serial.printf("Picture file name: %s\n", path.c_str());
#endif

  File file = fs.open(path.c_str(), FILE_WRITE);
  if(!file){
    DPRINTLN("Failed to open file in writing mode");
  } 
  else {
    file.write(fb->buf, fb->len); // payload (image), payload length
#ifdef DEBUG
    Serial.printf("Saved file to path: %s\n", path.c_str());
#endif
  }
  file.close();
  esp_camera_fb_return(fb); 
}

int setLED(int num) {
    if (num > 0) {
      num = 1;
      digitalWrite(LED_PIN,HIGH);
    }
    else {
      num = 0;
      digitalWrite(LED_PIN,LOW);
    }
    return num;
}

camera_fb_t * readImageFile(String path) {
  if (sdcard_present == 0) {
    return NULL;
  }
  
    fs::FS &fs = SD_MMC;          // sd card file system
    File file = fs.open(path, FILE_READ);
    if (file) {
      size_t fbLen = file.size();
      uint8_t *jpg_buffer = (uint8_t *)ps_malloc(fbLen);
      if (jpg_buffer) {
        file.read(jpg_buffer, fbLen);
        file.close();
        camera_fb_t * fb = (camera_fb_t*) ps_malloc(sizeof(camera_fb_t));
        fb->buf = jpg_buffer;
        fb->len = fbLen;
        fb->width = 320;
        fb->height = 240;
        fb->format = PIXFORMAT_JPEG;
        return fb;
      }
    }
    return NULL;
}

int getIntensity(uint8_t * rgb_buffer, int w, int c1, int c2, int r1, int r2) {
  int intensity = 0;
  for (int col = c1; col < c2; ++col) {
    for (int row = r1; row < r2; ++row) {
      intensity += rgb_buffer[3*w*row+3*col+0];
      intensity += rgb_buffer[3*w*row+3*col+1];
      intensity += rgb_buffer[3*w*row+3*col+2];
    }
  }
  return intensity;
}

void getIntensities(camera_fb_t * fb, int res[6]) {
  if (!fb) {
    return;
  }
  int width = 320;
  int height = 240;
  int len = width*height*3;
  uint8_t * rgb_buffer = (uint8_t *)ps_malloc(len);
  fmt2rgb888(fb->buf,fb->len,fb->format,rgb_buffer);
  res[0] = getIntensity(rgb_buffer, width, 130, 150, 75, 95);
  res[1] = getIntensity(rgb_buffer, width, 205, 225, 75, 95);
  res[2] = getIntensity(rgb_buffer, width, 130, 150, 142, 162);
  res[3] = getIntensity(rgb_buffer, width, 205, 225, 142, 162);
  res[4] = getIntensity(rgb_buffer, width, 130, 150, 209, 229);
  res[5] = getIntensity(rgb_buffer, width, 205, 225, 209, 229);
  free(rgb_buffer);
}

void drawDelay() {
  delay(100);
}

void drawLine(uint8_t x1, uint8_t y1, uint8_t x2, uint8_t y2, uint8_t color) {
  char buf[20];
  sprintf(buf, "!A L00000\r\n");
  buf[4] = x1 + 40; buf[5] = y1 + 40;
  buf[6] = x2 + 40;
  buf[7] = y2 + 40;
  buf[8] = color + 40;
  Serial2.print(buf);
  Serial.println("Sent " + String(buf) + " " + String(x1) + " " + String(y1) + " " + String(x2) + " " + String(y2) + " " + String(color));
  drawDelay();
}

void drawText(int16_t x, int16_t y, const char * s) {
  char buf[20];
  sprintf(buf, "!A T00%s\r\n", s);
  buf[4] = x + 40; buf[5] = y + 40;
  Serial2.print(buf);
  Serial.println("Sent " + String(buf) + " " + String(x) + " " + String(y));
  drawDelay();
}

void drawFastVLine(int16_t x, int16_t y, int16_t h, uint16_t color) {
  char buf[20];
  sprintf(buf, "!A V0000\r\n");
  buf[4] = x + 40; buf[5] = y + 40;
  buf[6] = h + 40;
  buf[7] = color + 40;
  Serial2.print(buf);
  Serial.println("Sent " + String(buf) + " " + String(x) + " " + String(y) + " " + String(h) + " " + String(color));
  drawDelay();
}

void drawFastHLine(int16_t x, int16_t y, int16_t w, uint16_t color) {
  char buf[20];
  sprintf(buf, "!A H0000\r\n");
  buf[4] = x + 40; buf[5] = y + 40;
  buf[6] = w + 40;
  buf[7] = color + 40;
  Serial2.print(buf);
  Serial.println("Sent " + String(buf) + " " + String(x) + " " + String(y) + " " + String(w) + " " + String(color));
  drawDelay();
}
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

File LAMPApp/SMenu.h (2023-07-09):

#include <PIDController.h>
#include <SoftwareSerial.h>
#include <CommandHandler.h>

SoftwareSerial serial2(12, 13); // RX, TX
// 1. Maximum number of Commands = 10
// 2. Maximum command length = 30
// 3. Maximum number of Variables = 15
// 4. Start of Message = !
// 5. End of Message = \r
CommandHandler<4, 20, 0> SerialCommandHandler(serial2, '!', '\n');

// Mosfet Pin
#define mosfet_pin 9

#define encoder0Press  2
#define encoder0PinA  3
#define encoder0PinB  4
volatile unsigned int encoder0Pos = 0;
volatile unsigned int lastEncoder0Pos = 0;
bool encoderPrevA=true, encoderPrevB = true;

#define __Kp 200 // 500 // 30 // Proportional constant
#define __Ki 1 // 0.1 // 0.7 // Integral Constant
#define __Kd 10 // 100 // 200 // Derivative Constant
uint8_t set_temperature = 60;
float temperature_value_c = 60.0; // stores temperature value
PIDController pid; // Create an instance of the PID controller class, called "pid"
uint8_t tindex = 0;
uint8_t toutput = 0;

#define ThermistorPin 1
#define __R1 100000
#define __R2(x) (__R1 * x /(1024.0 - x))
#define __c1 0.00166736
#define __c2 0.000113695
#define __c3 2.57974e-07

#define MAIN_MENU 1
#define TEMP_MENU 2
#define INFO_MENU 3

uint8_t encoder_btn_count = 0;
unsigned long debounce = 0; // Debounce delay

byte menuState = MAIN_MENU;
byte menuCount = 1;
byte dir = 0;
bool runState = false;
bool enter_info = true;
byte camera_status = 0;
byte _s_ip[4];

void mainMenu() {
  display.clearDisplay();
  display.setTextSize(2);
  display.setTextColor(WHITE);

  display.setCursor(10, 0);
  display.println(F("Main"));
  //---------------------------------
  display.setTextSize(1);
  display.setCursor(10, 20);
  display.print(F("Info "));
  display.print(toutput, DEC);
  display.print(F(" "));
  display.print(tindex, DEC);
  
  display.setCursor(10, 30);
  display.print(F("Set Temp: "));
  // display.print(temperature_value_c, 1); // This causes some unwanted points in the display at the bottom right corner
  display.print((int)temperature_value_c);
  display.print(F("."));
  display.print((int) abs((temperature_value_c - (int)temperature_value_c) * 10));
  display.print(F("C"));

  if (runState) {
    display.setCursor(10, 40);
    display.print(F("Stop "));
  }
  else {
    display.setCursor(10, 40);
    display.print(F("Run "));
  }
  display.print(camera_status, DEC);
  display.print(F(" "));
  display.print(_s_ip[0], DEC);
  display.print(F("."));
  display.print(_s_ip[1], DEC);
  display.print(F("."));
  display.print(_s_ip[2], DEC);
  display.print(F("."));
  display.print(_s_ip[3], DEC);

  display.setCursor(2, (menuCount * 10) + 10);
  display.println(F(">"));

  display.display();
}

void tempMenu() {
  display.clearDisplay();
  display.setTextSize(2);
  display.setTextColor(WHITE);

  display.setCursor(10, 0);
  display.println(F("Temp C"));
  //---------------------------------
  display.setTextSize(1);
  display.setCursor(10, 20);
  display.print(F("Value:"));
  display.println(set_temperature, 1);

  display.setCursor(10, 30);
  display.println(F("Return"));

  display.setCursor(2, (menuCount * 10) + 10);
  display.println(F(">"));

  display.display();
}
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

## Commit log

2023-07-09 LAMP Device
    [Camera.brd, Camera.sch, LAMP.brd, LAMP.sch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]
2023-07-09 Arduino Codes

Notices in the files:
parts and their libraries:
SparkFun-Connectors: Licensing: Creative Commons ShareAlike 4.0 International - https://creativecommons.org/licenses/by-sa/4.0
